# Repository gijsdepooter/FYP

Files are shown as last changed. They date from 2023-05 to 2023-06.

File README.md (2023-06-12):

# FYP
Developing a Single Channel Ultrasound Device

This project is being done with the Imperial College London Bioengineering Department, in collaboration with Prof Manos Drakakis and PhD Momen Kamal Tageldeen

This is a Repo for all the relevant material that I am developing/using for a low cost US scanner.

There are a few main parts of the US hardware:

1. The Pulser 
2. The MUX
3. The VGA (voltage gain amplifier)
4. The ADC

**PULSER**

The pulser is responsible for sending high voltage pulses to the piezo transducers in the US probe. I am using the HV7361 from microchip. It takes simple 3 bit digital instructions. These controlls are sent from the raspberry pi pico using the PIO interface to achieve precise timings.

**VGA**

The VGA controlls the amplification of the US signal and corrects for an attenuation of approximately 1dB/MHz/cm in tissue. The TGC profile is set by the MCP4921 DAC, controlled over SPI.
This is a 12 bit DAC that is controlled using the PIO interface of the rapsberry pi pico to achieve the desired speed.

**ADC** 

This project uses the LTC2236, a 10 bit DAC that can sample up to 65Msps. The ADC has a parallel output. The raspberry pi zero is used to decode the parallel ouptut using DMA and the secondary memory interface (SMI). Most of the code that controlls the ADC is from https://github.com/jbentham/rpi, and merely adapted to suit the needs of the IC of choice.

**MUX**

The multiplexer unit is an optional IC to leverage the single channel architecture of this board to controll multiple transducer channels. This allows for constructing B-Mode images with linear and phased arrays.

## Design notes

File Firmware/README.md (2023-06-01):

This contains all the firmware that operate the ultrasound board

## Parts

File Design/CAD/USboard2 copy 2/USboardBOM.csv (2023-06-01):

Source: | /Users/gijsdepooter/Desktop/UROP/CAD/USboard2 copy 2/USboard1.kicad_sch
Date: | Wednesday, 22 March 2023 at 10:44:08
Tool: | Eeschema (7.0.0-0)
Generator: | /Applications/KiCad/KiCad.app/Contents/SharedSupport/plugins/bom_csv_grouped_by_value_with_fp.py
Component Count: | 113
Ref | Qnty | Value | Cmp name | Footprint | Description | SUPPLIER | Supplier Part Number | Manufacturer | Manufacturer Part Number | Link | https://www.mouser.co.uk/ProductDetail/KYOCERA-AVX/0603ZD106KAT2A?qs=c1aAEamvUYHQhwHZOF6y0Q%3D%3D
C1 | 1 | 10uF | C | Capacitor_SMD:C_0603_1608Metric | Unpolarized capacitor | Mouser | 581-0603ZD106KAT2A | KYOCERA AVX | 0603ZD106KAT2A |  | https://www.mouser.co.uk/ProductDetail/TAIYO-YUDEN/HMJ212DC7105KGHTE?qs=DPoM0jnrROVb%2F1HhwpJMeA%3D%3D
C22, C23 | 2 | 1uF 100VDC | C | Capacitor_SMD:C_0805_2012Metric | Unpolarized capacitor | Mouser | 963-MJ212DC7105KGHTE | TAIYO YUDEN | HMJ212DC7105KGHTE |  | https://www.mouser.co.uk/ProductDetail/TDK/C0603X5R1A103K030BA
C3 | 1 | 0.01uF | C | Capacitor_SMD:C_0603_1608Metric | Unpolarized capacitor | Mouser | 581-06035C103KAT4A | KYOCERA AVX | 06035C103KAT4A |  | https://www.mouser.co.uk/ProductDetail/KEMET/C0603C104K8RAC
C59 | 1 | 22pF | C | Capacitor_SMD:C_0603_1608Metric | Unpolarized capacitor | Mouser | 603-CC603FRNPO9BN220 | YAGEO | CC0603FRNPO9BN220
C4, C5, C6, C7, C8, C9, C10, C11, C13,C18, C19, C20, C21, C24, C43, C44, C45, C46, C47, C49, C53, C55, C57, C58, C61, C63 | 28 | 0.1uF 10VDC 10% | C | Capacitor_SMD:C_0603_1608Metric | Unpolarized capacitor | Mouser | 80-C0603C104K8RAC | KEMET | C0603C104K8RAC |  | https://www.mouser.co.uk/ProductDetail/KEMET/C0603C475K8PACTU
C12 | 1 | 4.7uF | C | Capacitor_SMD:C_0603_1608Metric | Unpolarized capacitor | Mouser | 791-0603X475K100CT | WALSIN | 0603X475K100CT |  | https://www.mouser.co.uk/ProductDetail/KEMET/C0603C225K8RAC7411
C14 | 1 | 2.2uF | C | Capacitor_SMD:C_0603_1608Metric | Unpolarized capacitor | Mouser | 80-C0603C225K8R7411 | KEMET | C0603C225K8RAC7411 |  | https://www.mouser.co.uk/ProductDetail/TDK/C1608X7R1A105K080AC?qs=NRhsANhppD%252BTxQoqW7Ms9Q%3D%3D
C2, C15, C16 | 3 | 1uF 10VDC 10% | C | Capacitor_SMD:C_0603_1608Metric | Unpolarized capacitor | Mouser | 810-C1608X7R1A105K | TDK | C1608X7R1A105K080AC |  | https://www.mouser.co.uk/ProductDetail/KEMET/C0603C560J8HACTU?qs=W0yvOO0ixfEdkeZ4v%2FOkOw%3D%3D
C17 | 1 | 56pF | C | Capacitor_SMD:C_0603_1608Metric | Unpolarized capacitor | Mouser | 80-C0603C560J8HACTU | KEMET | C0603C560J8HACTU |  | https://www.mouser.co.uk/ProductDetail/KEMET/C0603C102K8RACAUTO
C50, C52, C54, C56, C62 | 5 | 1nF | C | Capacitor_SMD:C_0603_1608Metric | Unpolarized capacitor | Mouser | 80-C0603C102K8RAUTO | KEMET | C0603C102K8RACAUTO |  | https://www.mouser.co.uk/ProductDetail/TAIYO-YUDEN/HMJ107BB7104KAHT
C48, C51 | 2 | 100nF 100VDC | C | Capacitor_SMD:C_0603_1608Metric | Unpolarized capacitor | Mouser | 963-HMJ107BB7104KAHT | TAIYO YUDEN | HMJ107BB7104KAHT |  | https://www.mouser.co.uk/ProductDetail/TAIYO-YUDEN/LMK107SD183JA-T?qs=PzICbMaShUflHcZ%2F40mWUQ%3D%3D
C60 | 1 | 18nF | C | Capacitor_SMD:C_0603_1608Metric | Unpolarized capacitor | Mouser | 80-C0603C183K4R | KEMET | C0603C183K4RACTU |  | https://uk.farnell.com/diodes-inc/bav99/diode-ss-dual-100v-0-3a-sot23/dp/1902422?CMP=KNC-GUK-GEN-SKU-MDC-Test787
D1, D2, D3 | 3 | BAV99 | BAV99 | Package_TO_SOT_SMD:SOT-23 | BAV99 High-speed switching diodes, SOT-23 | Farnell | 1902422 | DIODES INC | BAV99 |  | https://www.digikey.co.uk/en/products/detail/phoenix-contact/1751264/2511021
J1 | 1 | Screw_Terminal_01x04 | Screw_Terminal_01x04 | screwConn3:1751264 | TERM BLK 4POS SIDE ENT 3.5MM PCB | Digikey | 277-5744-ND | Pheonix Contact | 1751264 |  | https://www.mouser.co.uk/ProductDetail/Adafruit/2222?qs=GURawfaeGuDZD0rNtWpsaQ%3D%3D
J2 | 1 | Raspberry_Pi_2_3 | Raspberry_Pi_2_3 | Connector_PinSocket_2.54mm:PinSocket_2x20_P2.54mm_Vertical | expansion header for Raspberry Pi 2 & 3 | Mouser | 485-2222 | Adafruit | 2222 |  | https://uk.rs-online.com/web/p/coaxial-connectors/5265785?matchtype=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
J3, J5 | 2 | Conn_Coaxial | Conn_Coaxial | Connector_Coaxial:SMA_Amphenol_132289_EdgeMount | coaxial connector SMA | RS | 526-5785 |  | 526-5785 |  | https://www.mouser.co.uk/ProductDetail/Amphenol-FCI/10129381-912003BLF?qs=0lQeLiL1qyb2GJZ3J3Epuw%3D%3D
J4 | 1 | Conn_01x12_Pin | Conn_01x12_Pin | Connector_PinHeader_2.54mm:PinHeader_2x06_P2.54mm_Vertical | Generic connector, single row, 02x6 | Mouser | 649-1012938191203BLF | Amphenol FCI | 10129381-912003BLF |  | https://www.mouser.co.uk/ProductDetail/Harwin/M22-2510205?qs=vF78I%252BjhbY%2FHssMovH2Mxg%3D%3D&mgh=1&vip=1
JP1, JP3, JP4, JP5, JP9 | 5 | Jumper_2_Open | Jumper_2_Open | Connector_PinHeader_2.00mm:PinHeader_2x01_P2.00mm_Vertical | Headers & Wire Housings 2 PIN SIL VERTICAL GOLD PIN HEADER | Mouser | 855-M22-2510205 | Harwin | M22-2510205 |  | https://www.mouser.co.uk/ProductDetail/Harwin/M22-2510205?qs=vF78I%252BjhbY%2FHssMovH2Mxg%3D%3D&mgh=1&vip=1
JP2, JP6 | 2 | Jumper_2_Bridged | Jumper_2_Bridged | Connector_PinHeader_2.00mm:PinHeader_2x01_P2.00mm_Vertical | Headers & Wire Housings 2 PIN SIL VERTICAL GOLD PIN HEADER | Mouser | 855-M22-2510205 | Harwin | M22-2510205 |  | https://www.mouser.co.uk/ProductDetail/TE-Connectivity/2355182-3?qs=Cb2nCFKsA8qFdalzWsoTCg%3D%3D&mgh=1&vip=1
L2 | 1 | Ferrite | L | Inductor_SMD:L_0603_1608Metric | Ferrite bead | Farnell | BLM18B | Murata Electronics | BLM18BB470SN1D
JP7, JP8, JP10 | 3 | Jumper_3_Bridged12 | Jumper_3_Bridged12 | Connector_PinHeader_2.00mm:PinHeader_1x03_P2.00mm_Vertical | Jumper, 3-pole, pins 1+2 closed/bridged | Mouser | 571-2355182-3 | TE Connectivity | 2355182-3 |  | https://www.mouser.co.uk/ProductDetail/Murata-Electronics/BLM18BA750SN1D?qs=eF9MexBACzorpPRQANQXVw%3D%3D
L1, L6, L7, L8, L9 | 5 | 100nH | L | Inductor_SMD:L_0603_1608Metric | Inductor | Mouser | 81-BLM18BA750SN1D | Murata Electronics | BLM18BA750SN1D |  | https://www.mouser.co.uk/ProductDetail/YAGEO/RC0603FR-07100KL?qs=e1ok2LiJcmaihem8Va5%2Fsw%3D%3D
R1 | 1 | 100K | R | Resistor_SMD:R_0603_1608Metric | Resistor | Mouser | 603-RC0603FR-07100KL | YAGEO | RC0603FR-07100KL |  | https://www.mouser.co.uk/ProductDetail/YAGEO/RT0603DRE07105KL
R2 | 1 | 105K | R | Resistor_SMD:R_0603_1608Metric | Resistor | Mouser | 603-RT0603DRE07105KL | YAGEO | RT0603DRE07105KL |  | https://www.mouser.co.uk/ProductDetail/YAGEO/RP0603BRD071KL?qs=Y0Uzf4wQF3kpBssB5AIvYA%3D%3D
R3, R4, R5, R6, R7 | 5 | 1K | R | Resistor_SMD:R_0603_1608Metric | Resistor | Mouser | 603-RP0603BRD071KL | YAGEO | RP0603BRD071KL |  | https://www.mouser.co.uk/ProductDetail/EPCOS-TDK/B82496C3101J
R8 | 1 | 49.9 | R | Resistor_SMD:R_0603_1608Metric | Resistor | Mouser | 667-ERJ-PA3F49R9V | Panasonic | ERJ-PA3F49R9V |  | https://www.mouser.co.uk/ProductDetail/YAGEO/RC0603FR-0718RL?qs=VU8sRB4EgwB41f75pR1ITg%3D%3D
R9, R10 | 2 | 18 | R | Resistor_SMD:R_0603_1608Metric | Resistor | Mouser | 603-RC0603FR-0718RL | YAGEO | RC0603FR-0718RL |  | https://www.mouser.co.uk/ProductDetail/YAGEO/RC0603FR-0733RL?qs=diQw95jMAeMotgif2GSHTQ%3D%3D
R11, R12, R13, R14, R15, R16, R17, R18, R19, R20, R21, R22, R23, R24, R25, R26 | 16 | 33 | R | Resistor_SMD:R_0603_1608Metric | Resistor | Mouser | 71-CRCW060333R0FKEAH | vISHAY / Dale | CRCW060333R0FKEAHP |  | https://www.mouser.co.uk/ProductDetail/Vishay-Dale/CRCW06034K70FKTA?qs=oYilhPf8E59EDJILyU4xpQ%3D%3D
R29, R30 | 2 | 4.7K | R | Resistor_SMD:R_0603_1608Metric | Resistor | Mouser | 71-CRCW0603-4.7K | Vishay / Draloric | CRCW06034K70FKTA |  | https://www.mouser.co.uk/ProductDetail/YAGEO/RC0603FR-0710KL?qs=grNVn54RoB%252B3GtjbJj3wJQ%3D%3D
R31, R41, R42, | 3 | 10K | R | Resistor_SMD:R_0603_1608Metric | Resistor | Mouser | 603-RC0603FR-0710KL | YAGEO | RC0603FR-0710KL |  | https://www.mouser.co.uk/ProductDetail/Bourns/CR0603-FX-1000ELF?qs=K5ddiUFZPT7prY7pGcr1LQ%3D%3D
R37, R38 | 2 | 100 | R | Resistor_SMD:R_0603_1608Metric | Resistor | Mouser | 652-CR0603FX-1000ELF | Bourns | CR0603-FX-1000ELF |  | https://www.mouser.co.uk/ProductDetail/YAGEO/AC0603FR-0711KL?qs=sGAEpiMZZMtlubZbdhIBINBo7nw4llFtNj40dcv4WFE%3D
R39 | 1 | 11k | R | Resistor_SMD:R_0603_1608Metric | Resistor | Mouser | 603-AC0603FR-0711KL | YAGEO | AC0603FR-0711KL |  | https://www.mouser.co.uk/ProductDetail/YAGEO/AC0603FR-07280RL
R43 | 1 | 280 | R | Resistor_SMD:R_0603_1608Metric | Resistor | Mouser | 603-AC0603FR-07280RL | YAGEO | AC0603FR-07280RL |  | https://www.mouser.co.uk/ProductDetail/Microchip-Technology-Atmel/MD0100N8-G?qs=0AMA1uIX0FIE5iDlCsAHAw%3D%3D
U2 | 1 | MD0100N8-G | MD0100N8-G | MDO100:MD0100N8-G | T/R protection switch | Mouser | 689-MD0100N8-G | Microchip | MD0100N8-G |  | https://www.mouser.co.uk/ProductDetail/Microchip-Technology/MCP4725A3T-E-CH?qs=hH%252BOa0VZEiBSYoLvaYdGYg%3D%3D
U4 | 1 | MCP4725A3T-E/CH | MCP4725A3T-E/CH | Package_TO_SOT_SMD:SOT-23-6 | 12-bit Digital-to-Analog Converter, integrated EEPROM, I2C interface, SOT-23-6 | Mouser | 579-MCP4725A3T-E/CH | Microchip | MCP4725A3T-E/CH |  | https://www.mouser.co.uk/ProductDetail/Analog-Devices/LT1763IS8-3.3PBF?qs=ytflclh7QUXoCHefIThm8A%3D%3D
U5 | 1 | LT1763IS8-3.3-PBF | LT1763IS8-3.3-PBF | VCCsup:LT1763IS8-3.3-PBF | Voltage regulator | Mouser | 584-LT1763IS8-3.3PBF | Analog Devices | LT1763IS8-3.3#PBF |  | https://dk.farnell.com/en-DK/on-semiconductor/nc7svu04p5x/inverter-gate-single-1-i-p-sc/dp/2453123
U6 | 1 | NC7SVU04P5X | NC7SVU04P5X | INVERTER:NC7SVU04P5X | Inverter | Farnell | 2453123 | ONSEMI | NC7SVU04P5X
U1 | 1 | LTC2236IUH-PBF | LTC2236:LTC2236IUH-PBF | ADC 25MSPS 10BIT |  | Mouser | 584-LTC2236IUH#PBF | Analog Devices | LTC2236IUH#PBF |  | £9.64 | https://www.mouser.co.uk/ProductDetail/Analog-Devices/LTC2236CUHPBF?qs=hVkxg5c3xu9mjIScvNp8xw%3D%3D
U3 | 1 | 74VCX16373MTD | Latch:74VCX16373MTD | LOGIC LATCH |  | Mouser | 512-74VCX16373MTD | onsemi / Fairchild | 74VCX16373MTD |  | £1.73 | https://www.mouser.co.uk/ProductDetail/onsemi-Fairchild/74VCX16373MTD?qs=bX5Pkui%252BodUH7A1197lniw%3D%3D
U7 | 1 | HV7361GA-G | HV7361:HV7361GA-G | PULSER |  | Mouser | 579-HV7361GA-G | Microchip | HV7361GA-G |  | £8.98 | https://www.mouser.co.uk/ProductDetail/579-HV7361GA-G
U11 | 1 | AD8331ARQZ | AD8331:SOP64P600X175-20N | AD8331ARQZ, Programmable Gain Amplifier, 20-Pin QSOP |  | Mouser | 584-AD8331ARQZ | Analog Devices | AD8331ARQZ |  | £12.44 | https://www.mouser.co.uk/ProductDetail/Analog-Devices/AD8331ARQZ-R7?qs=%2FtpEQrCGXCysgac2siIaMw%3D%3D

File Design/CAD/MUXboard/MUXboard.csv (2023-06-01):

Source: | /Users/gijsdepooter/Desktop/Desktop - Gijs’s MacBook Pro/UROP/MUXboard/MUXboard.kicad_sch
Date: | Monday, 24 April 2023 at 08:52:58
Tool: | Eeschema (7.0.0-0)
Generator:
Component Count: | 9
Ref | Qnty | Value | Cmp name | Description | Supplier | Supplier Part Number | Manufacturer | MPN
C1, C2 | 2 | 1u | C | Unpolarized capacitor | Mouser | 810-C1608X7R1A105K | TDK | C1608X7R1A105K080AC | https://www.mouser.co.uk/ProductDetail/TDK/C1608X7R1A105K080AC?qs=NRhsANhppD%252BTxQoqW7Ms9Q%3D%3D
IC1 | 1 | HV2607T-C_R8X | HV2607T-C_R8X | HV2607T-C/R8X | Digikey | 150-HV2607T-C/R8XTR-ND | Microchip Technology | HV2607T-C/R8X
J1, J2 | 2 | Conn_Coaxial | Conn_Coaxial_1 | coaxial connector SMA | RS | 180-9922 | Wurth Elektronik | 6.03142E+13 | https://uk.rs-online.com/web/p/coaxial-connectors/1809922
J4 | 1 | Conn_01x16_Pin | Conn_01x16_Pin | Generic connector, single row, 01x16, script generated | Mouser | 200-TSW10808LD | Samtec | TSW-108-08-L-D | https://www.mouser.co.uk/ProductDetail/Samtec/TSW-108-08-L-D?qs=rU5fayqh%252BE3wWhrtuP8e1w%3D%3D
J5 | 1 | Conn_01x12_Pin | Conn_01x12_Pin | Generic connector, single row, 01x12, script generated | Mouser | 649-1012938191203BLF | Amphenol FCI | 10129381-912003BLF | https://www.mouser.co.uk/ProductDetail/Amphenol-FCI/10129381-912003BLF?qs=0lQeLiL1qyb2GJZ3J3Epuw%3D%3D
JP1 | 1 | Jumper_2_Open | Jumper_2_Open | Jumper, 2-pole, open | Mouser | 855-M22-2510205 | Harwin | M22-2510205 | https://www.mouser.co.uk/ProductDetail/Harwin/M22-2510205?qs=vF78I%252BjhbY%2FHssMovH2Mxg%3D%3D
R1, R2, R3, R4, R5 | 5 | 10K | R | Resistor | Mouser | 603-RC0603FR-0710KL | YAGEO | RC0603FR-0710KL | https://www.mouser.co.uk/ProductDetail/YAGEO/RC0603FR-0710KL?qs=grNVn54RoB%252B3GtjbJj3wJQ%3D%3D

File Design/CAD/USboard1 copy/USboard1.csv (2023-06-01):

chip | quantity | name |  |  |  | link
U1 | 1 | LTC2236IUH-PBF | LTC2236:LTC2236IUH-PBF | ADC 25MSPS 10BIT | Mouser | https://www.mouser.co.uk/ProductDetail/Analog-Devices/LTC2236CUHPBF?qs=hVkxg5c3xu9mjIScvNp8xw%3D%3D
U2 | 1 | MD0100N8-G | MDO100:MD0100N8-G | T/R SWITCH | Mouser | https://www.mouser.co.uk/ProductDetail/Microchip-Technology-Atmel/MD0100N8-G?qs=0AMA1uIX0FIE5iDlCsAHAw%3D%3D
U3 | 1 | 74VCX16373MTD | Latch:74VCX16373MTD | LOGIC LATCH | Mouser | https://www.mouser.co.uk/ProductDetail/onsemi-Fairchild/74VCX16373MTD?qs=bX5Pkui%252BodUH7A1197lniw%3D%3D
U4 | 1 | MCP4725A3T-E/CH | Package_TO_SOT_SMD:SOT-23-6 | 12-bit Digital-to-Analog Converter, integrated EEPROM, I2C interface, SOT-23-6 | Mouser | https://www.mouser.co.uk/ProductDetail/Microchip-Technology/MCP4725A3T-E-CH?qs=hH%252BOa0VZEiBSYoLvaYdGYg%3D%3D
U10 | 1 | HV7361GA-G | HV7361:HV7361GA-G | PULSER | Mouser | https://www.mouser.co.uk/ProductDetail/579-HV7361GA-G
U11 | 1 | AD8331ARQZ | AD8331:SOP64P600X175-20N | AD8331ARQZ, Programmable Gain Amplifier, 20-Pin QSOP | Mouser | https://www.mouser.co.uk/ProductDetail/Analog-Devices/AD8331ARQZ-R7?qs=%2FtpEQrCGXCysgac2siIaMw%3D%3D

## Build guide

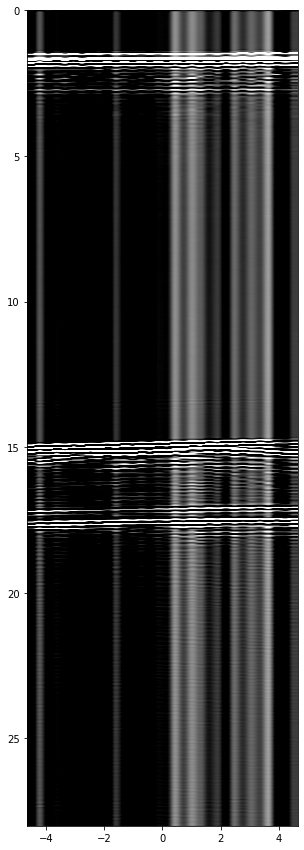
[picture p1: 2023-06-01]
Image_construction/Figure 2022-07-15 182849.png

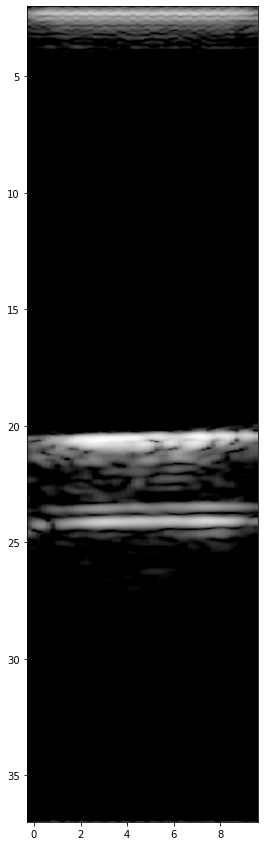
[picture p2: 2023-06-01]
Image_construction/Figure 2022-07-19 131949.png

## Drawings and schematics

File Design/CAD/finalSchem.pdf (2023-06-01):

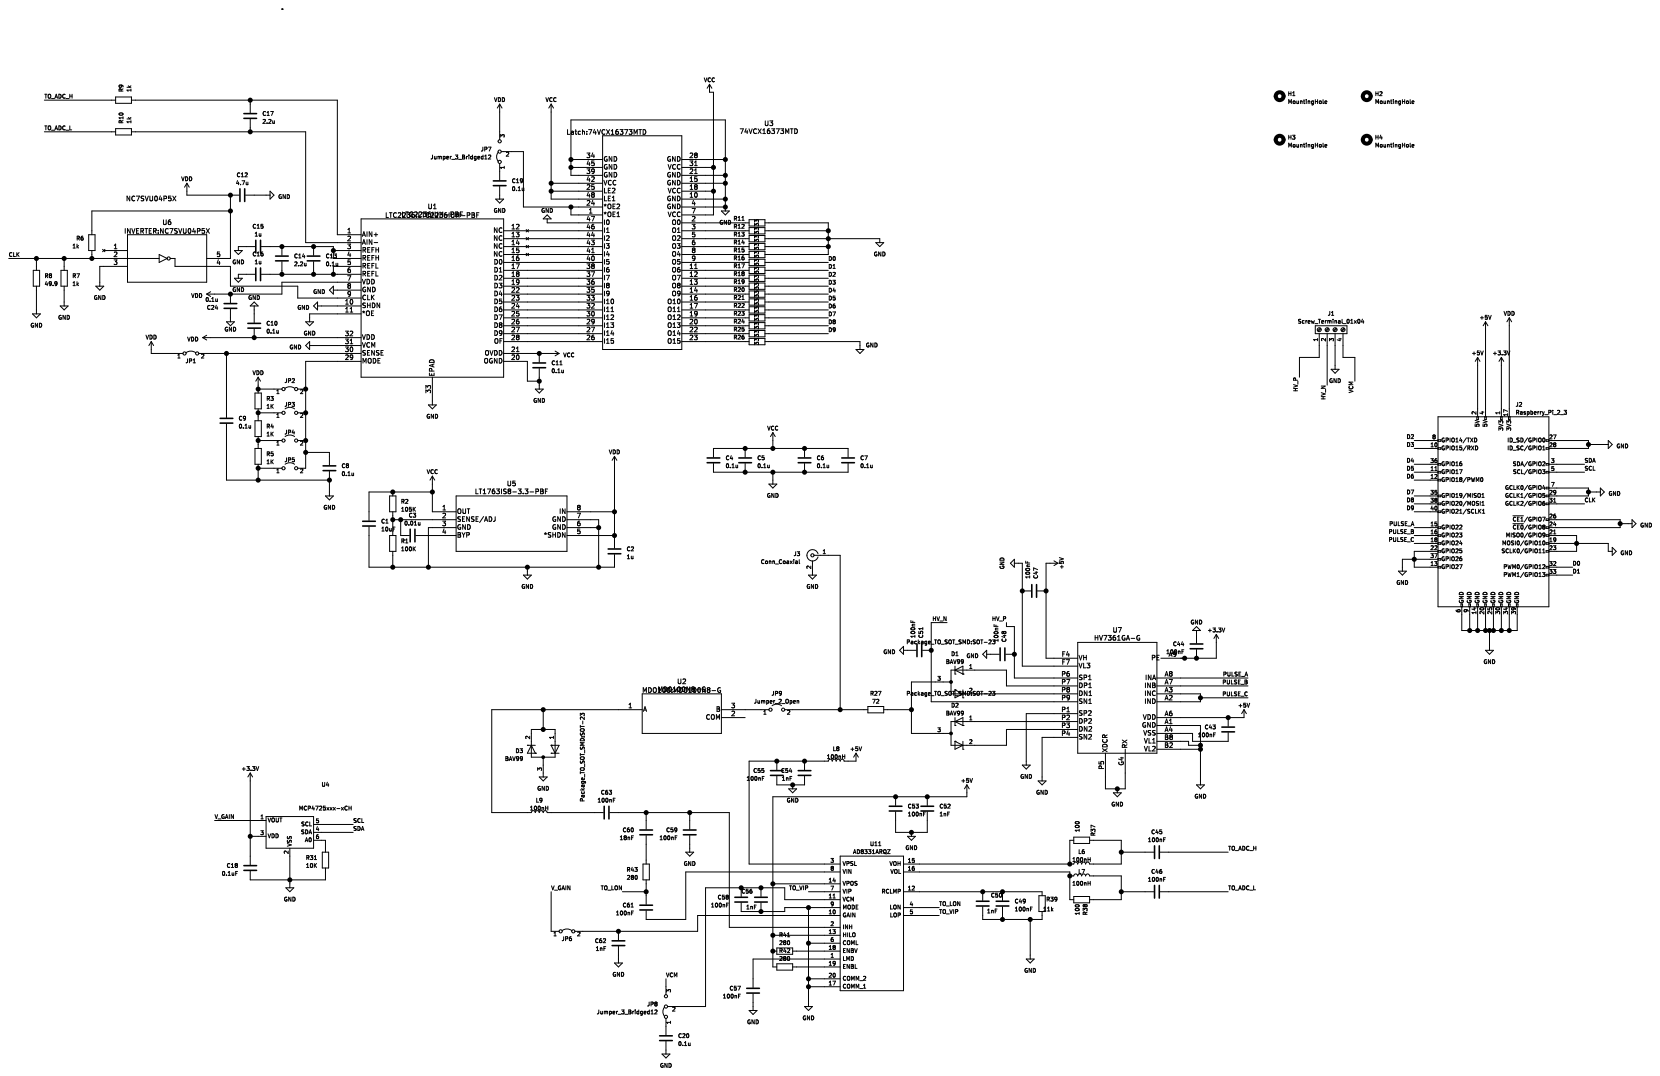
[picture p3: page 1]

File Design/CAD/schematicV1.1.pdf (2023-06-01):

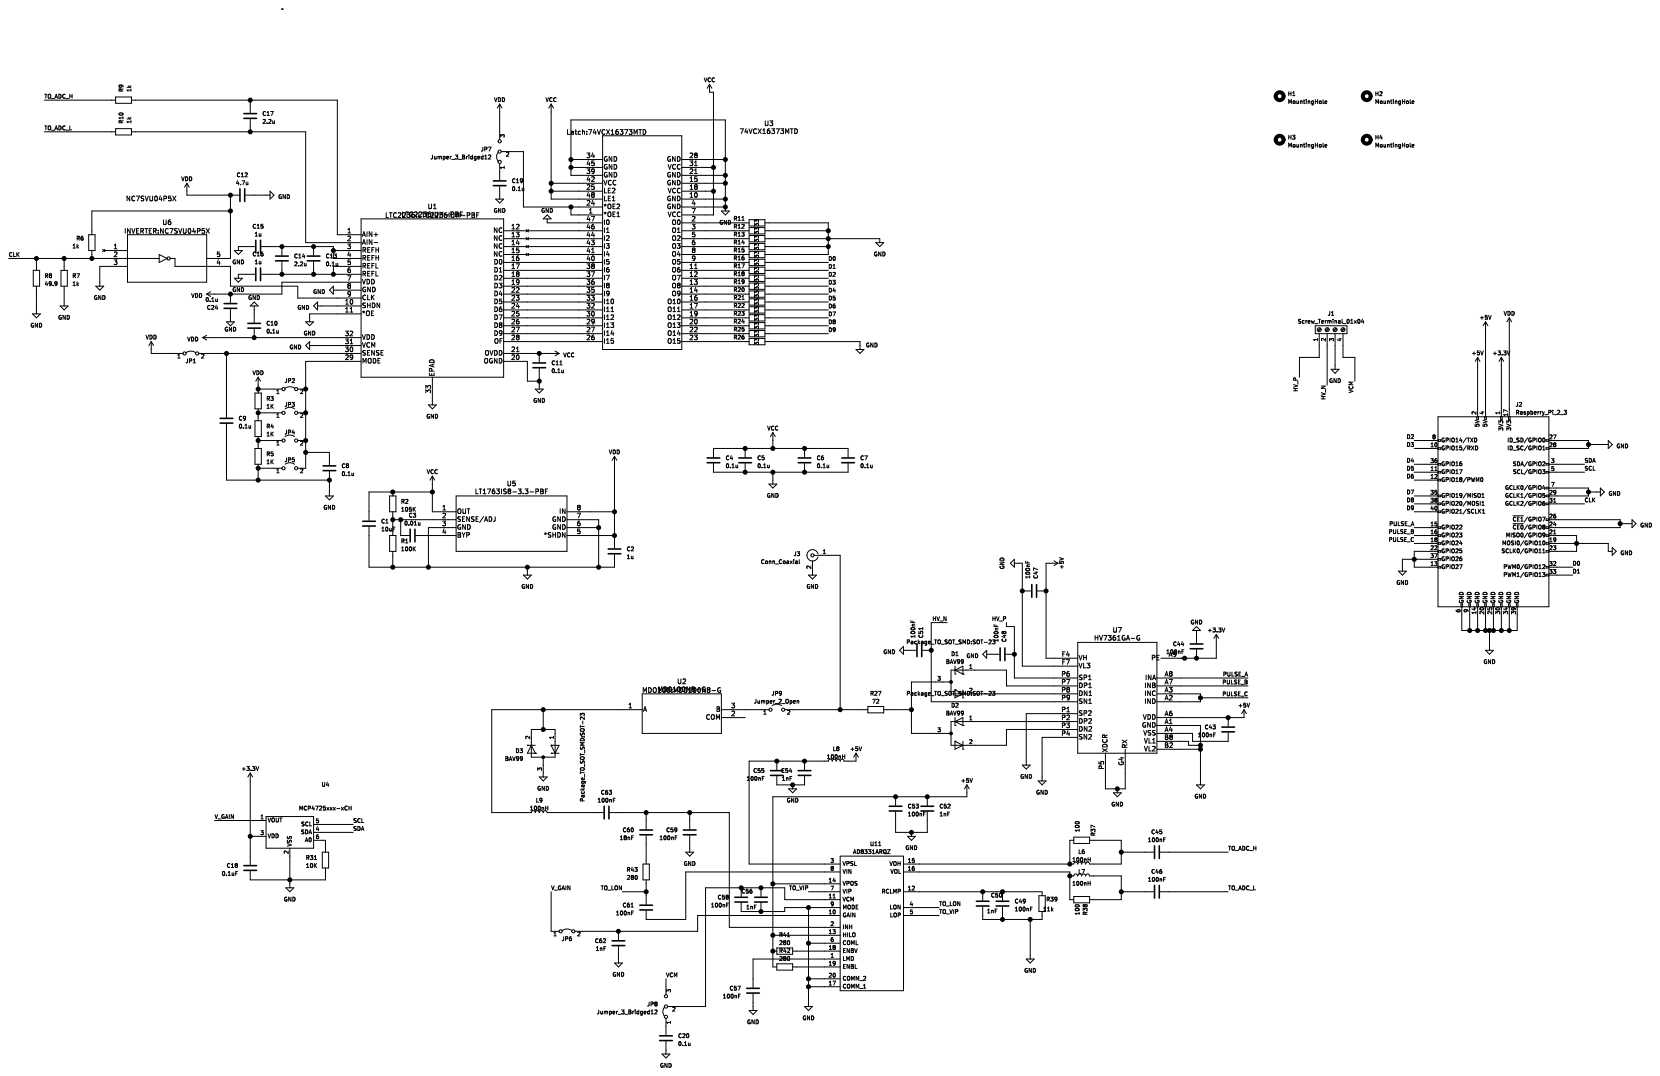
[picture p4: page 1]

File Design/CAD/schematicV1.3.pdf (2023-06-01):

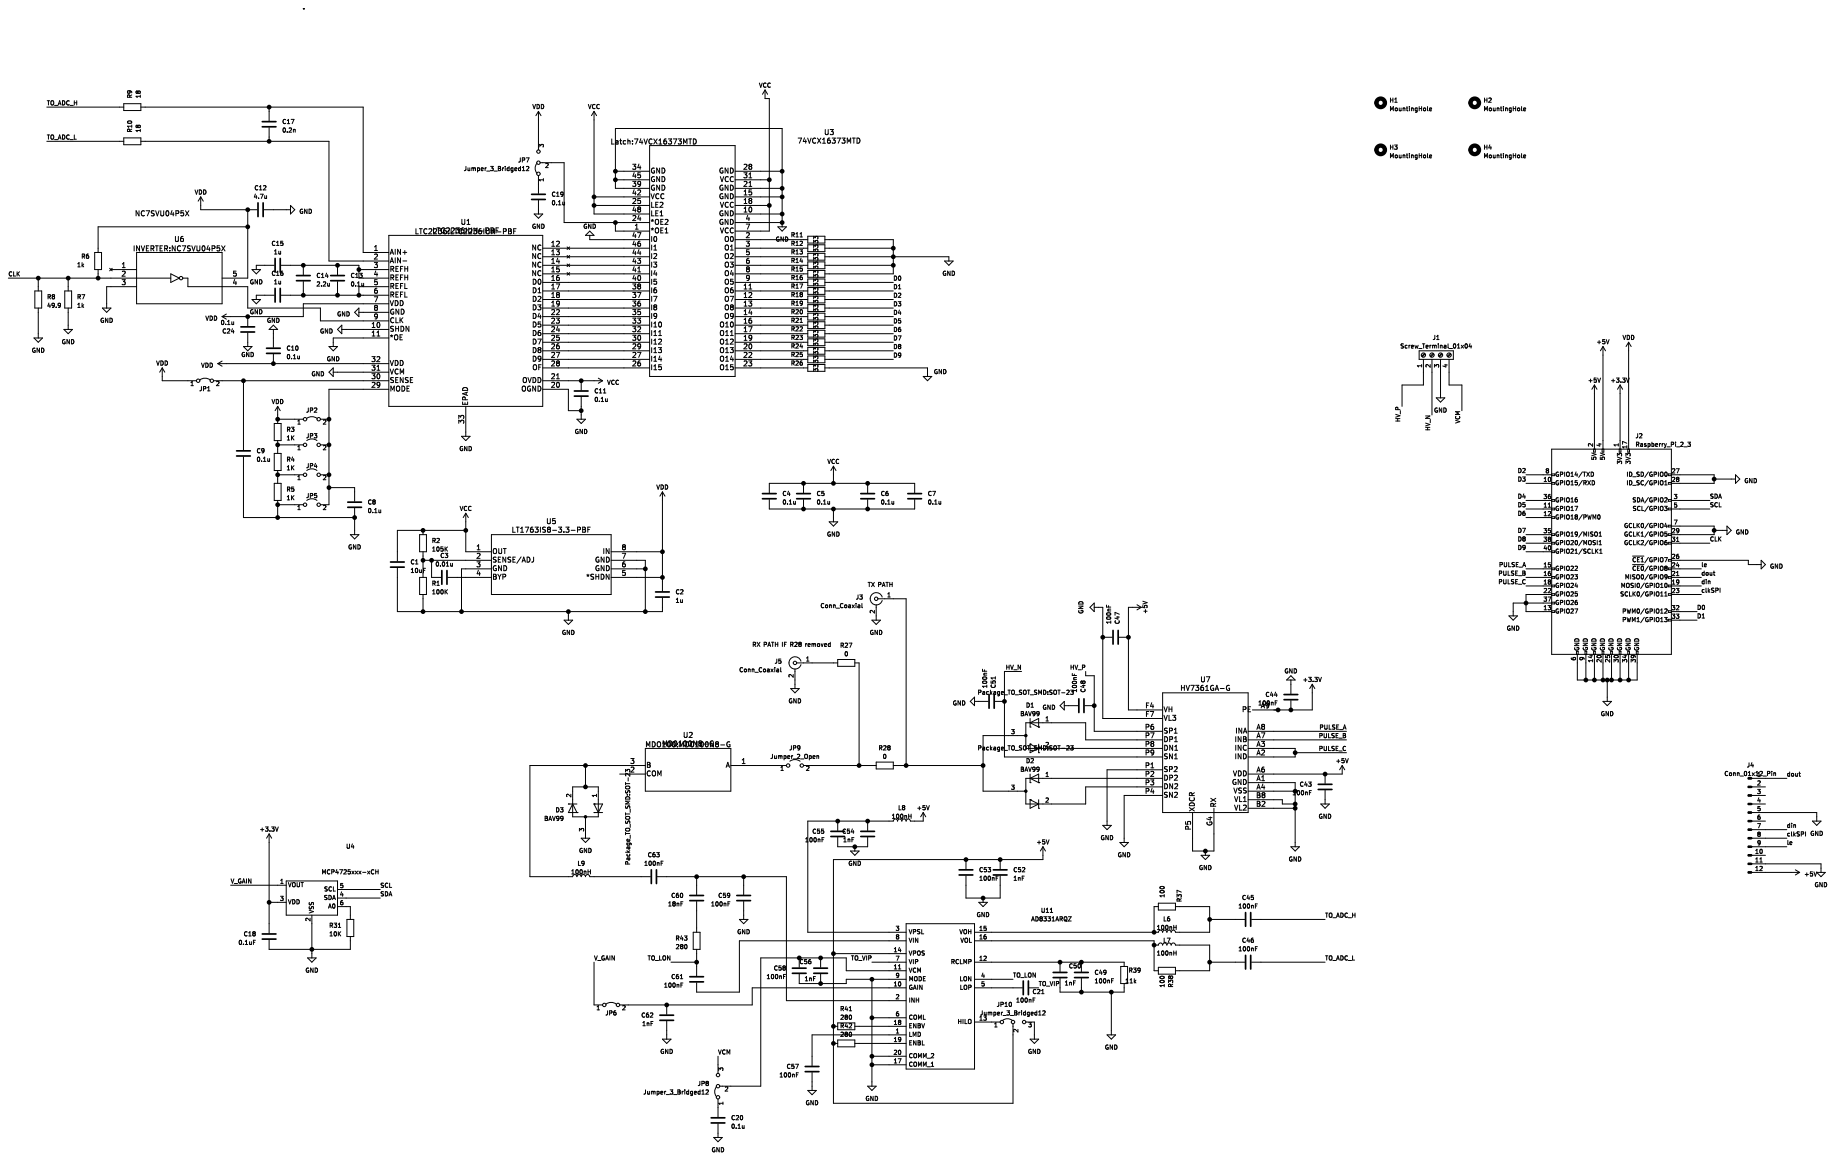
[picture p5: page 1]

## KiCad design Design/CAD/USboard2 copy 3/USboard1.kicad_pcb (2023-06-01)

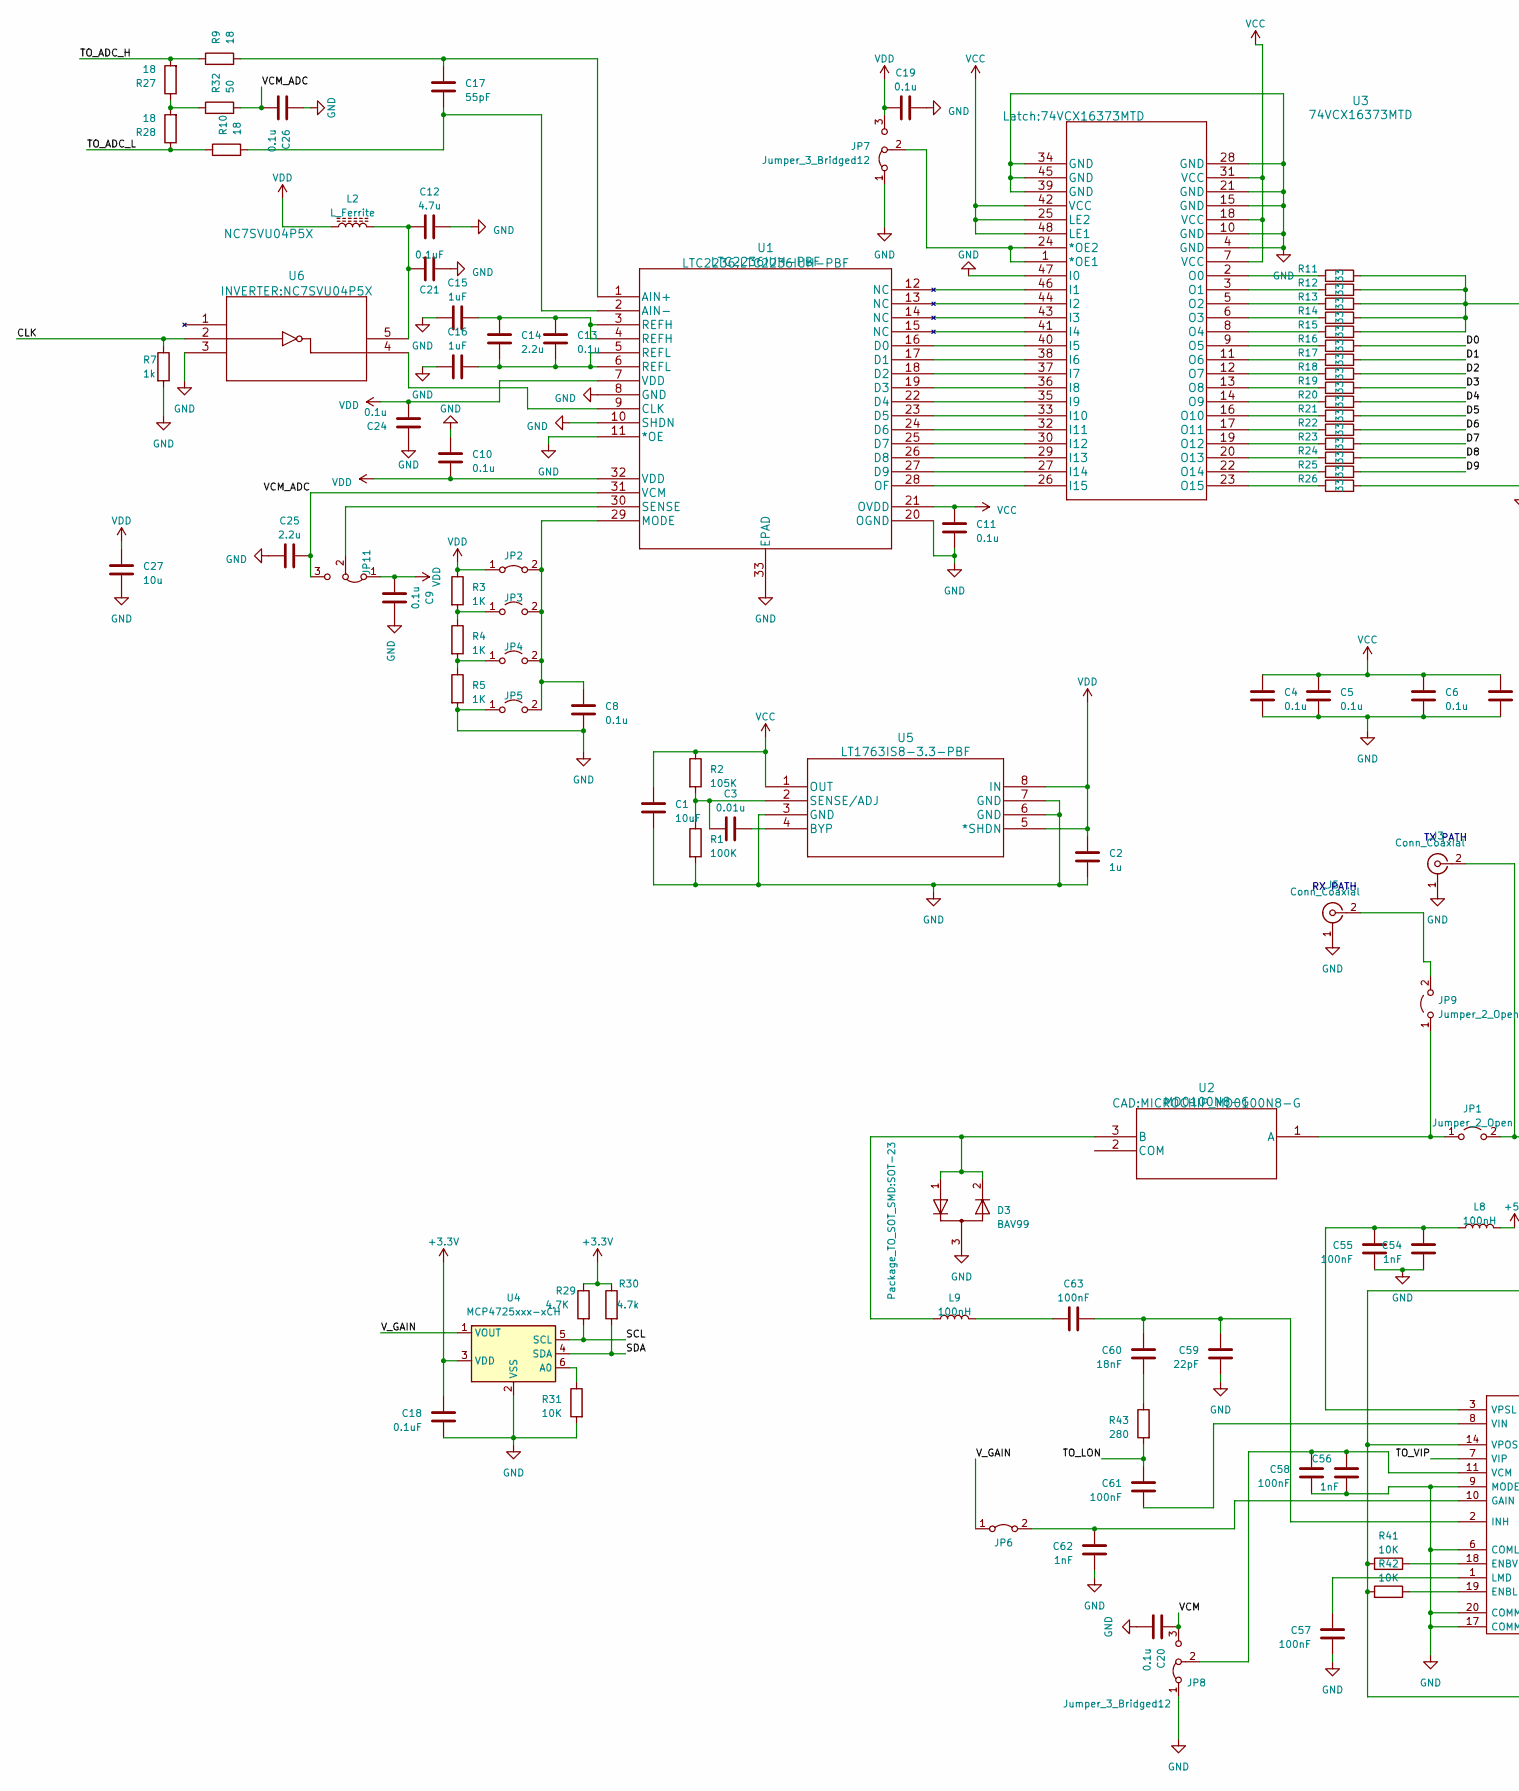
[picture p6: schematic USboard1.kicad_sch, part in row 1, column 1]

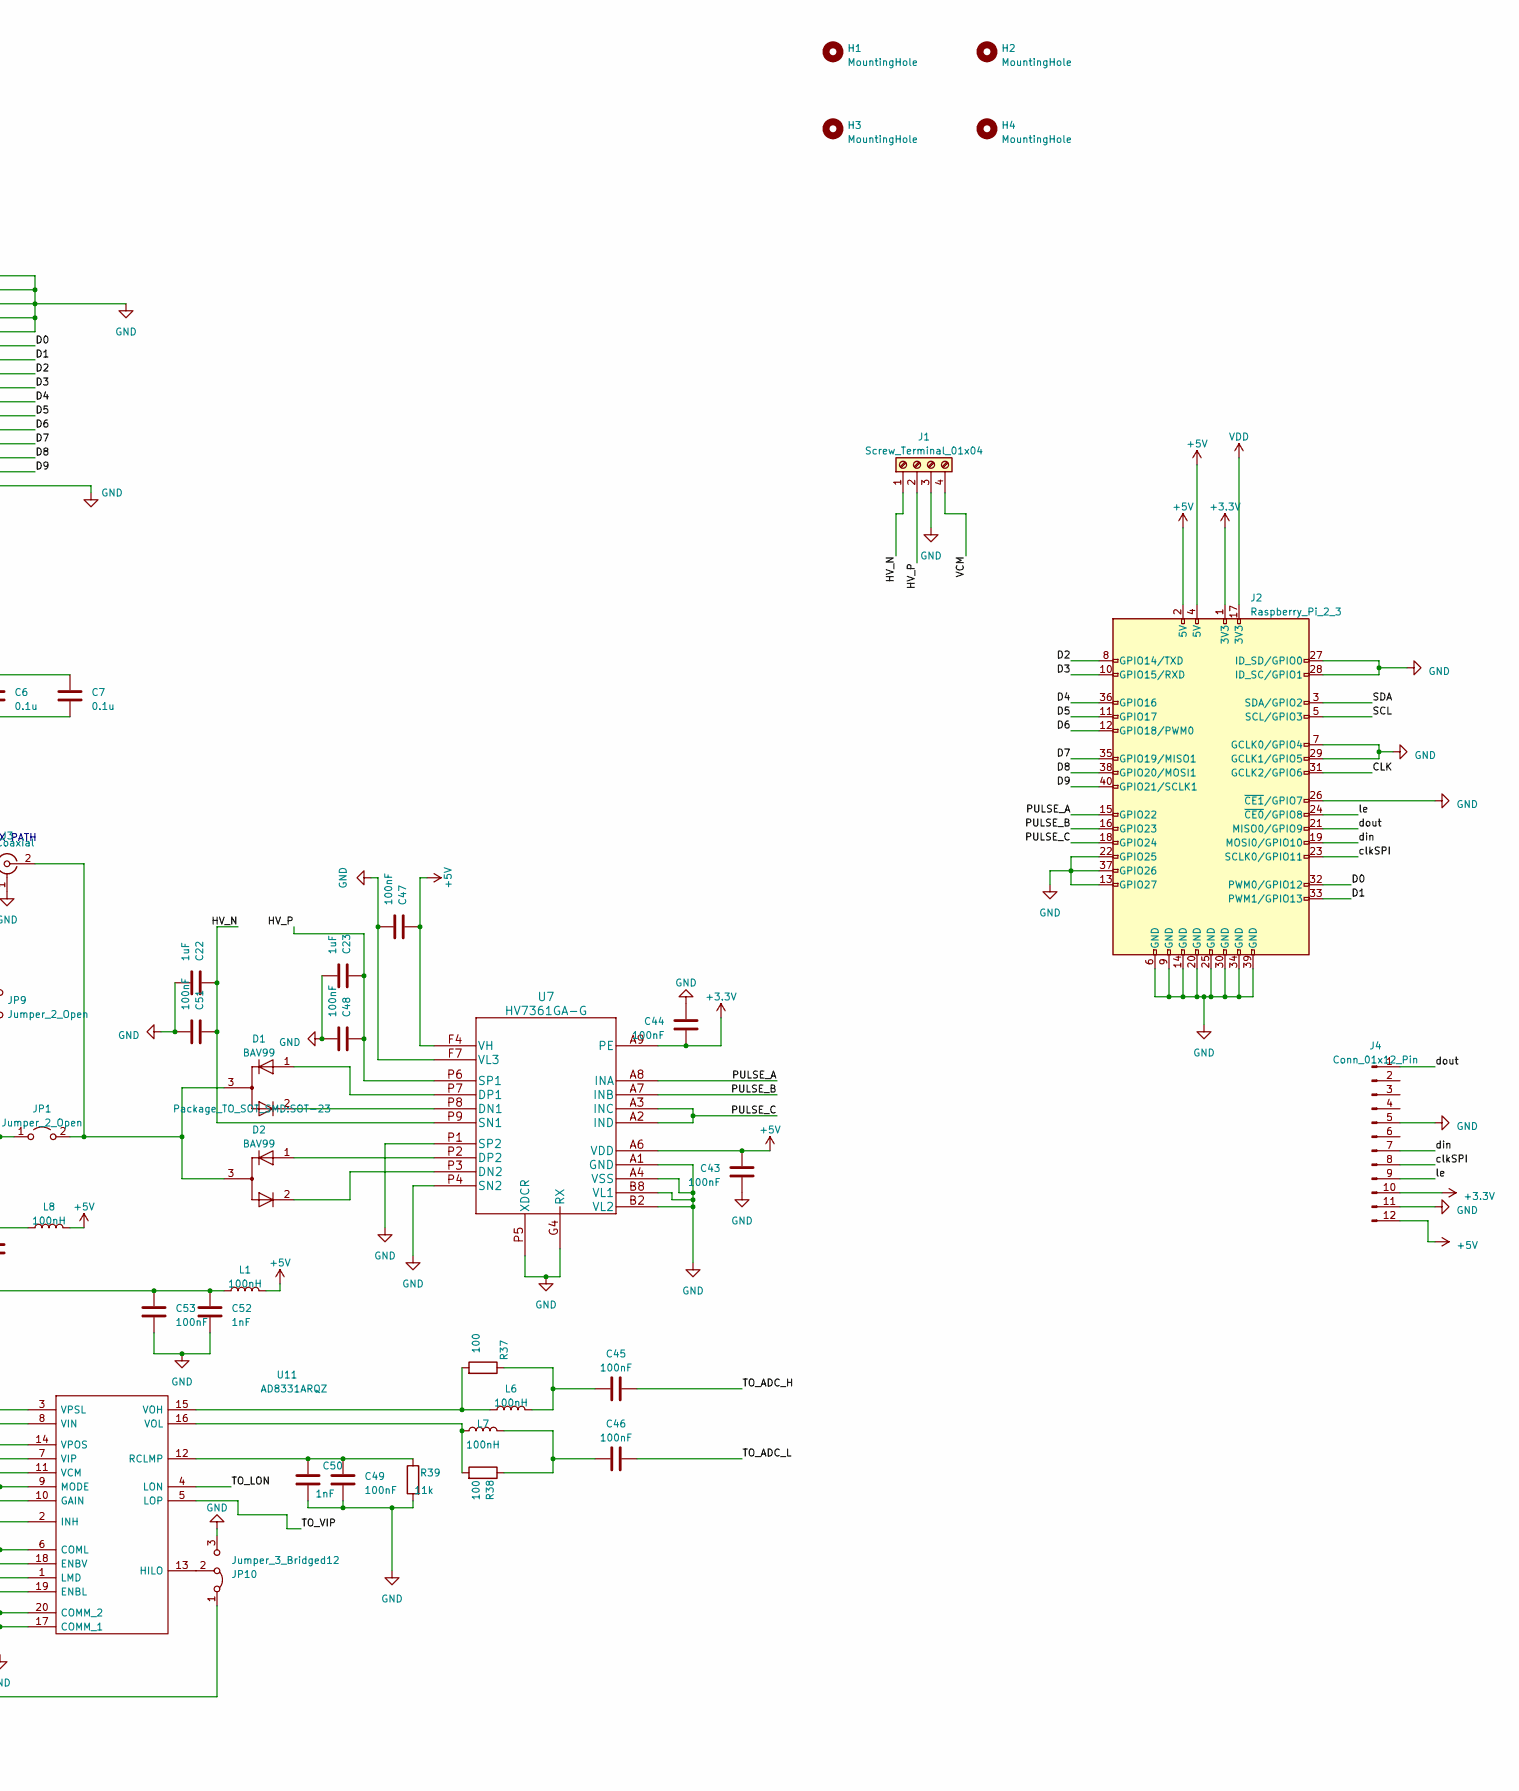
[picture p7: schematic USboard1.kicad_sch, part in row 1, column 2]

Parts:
C1: 10uF; C_0603_1608Metric
C2: 1u; C_0603_1608Metric
C3: 0.01u; C_0603_1608Metric
C4, C5, C6, C7, C8, C9, C10, C11, C13, C19, C20, C24, C26: 0.1u; C_0603_1608Metric
C12: 4.7u; C_0603_1608Metric
C14, C25: 2.2u; C_0603_1608Metric
C15, C16: 1uF; C_0603_1608Metric
C17: 55pF; C_0603_1608Metric
C18, C21: 0.1uF; C_0603_1608Metric
C22, C23: 1uF; C_0805_2012Metric
C27: 10u; C_0603_1608Metric
C43, C44, C45, C46, C47, C48, C49, C51, C53, C55, C57, C58, C61, C63: 100nF; C_0603_1608Metric
C50, C52, C54, C56, C62: 1nF; C_0603_1608Metric
C59: 22pF; C_0603_1608Metric
C60: 18nF; C_0603_1608Metric
D1, D2, D3: BAV99; SOT-23
H1, H2, H3, H4: MountingHole; MountingHole_3.5mm
J1: Screw_Terminal_01x04; 1751264
J2: Raspberry_Pi_2_3; PinSocket_2x20_P2.54mm_Vertical
J3, J5: Conn_Coaxial; RS_526-5785
J4: Conn_01x12_Pin; PinHeader_2x06_P2.54mm_Vertical
JP1, JP3, JP4, JP5, JP9: Jumper_2_Open; PinHeader_2x01_P2.00mm_Vertical
JP2, JP6: Jumper_2_Bridged; PinHeader_2x01_P2.00mm_Vertical
JP7, JP8, JP10, JP11: Jumper_3_Bridged12; PinHeader_1x03_P2.00mm_Vertical
L1, L6, L7, L8, L9: 100nH; L_0603_1608Metric
L2: L_Ferrite; L_0603_1608Metric
R1: 100K; R_0603_1608Metric
R2: 105K; R_0603_1608Metric
R3, R4, R5: 1K; R_0603_1608Metric
R7: 1k; R_0603_1608Metric
R9, R10, R27, R28: 18; R_0603_1608Metric
R11, R12, R13, R14, R15, R16, R17, R18, R19, R20, R21, R22, R23, R24, R25, R26: 33; R_0603_1608Metric
R29: 4.7K; R_0603_1608Metric
R30: 4.7k; R_0603_1608Metric
R31, R41, R42: 10K; R_0603_1608Metric
R32: 50; R_0603_1608Metric
R37, R38: 100; R_0603_1608Metric
R39: 11k; R_0603_1608Metric
R43: 280; R_0603_1608Metric
U1: LTC2236IUH-PBF
U2: MD0100N8-G; MICROCHIP_MD0100N8-G
U3: 74VCX16373MTD
U4: MCP4725xxx-xCH; SOT-23-6
U5: LT1763IS8-3.3-PBF
U6: NC7SVU04P5X
U7: HV7361GA-G
U11: AD8331ARQZ; SOP64P600X175-20N; Manufacturer_Part_Number AD8331ARQZ; Mouser Part Number 584-AD8331ARQZ

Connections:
+3.3V: C18.1, C44.2, J2.1 (3V3), J4.10, R29.1, R30.1, U4.3 (VDD), U7.A9 (PE)
+5V: C43.1, C47.1, J2.2 (5V), J2.4 (5V), J4.12, L1.1, L8.1, U7.A6 (VDD), U7.F4 (VH)
/CLK: J2.31 (GCLK2/GPIO6), R7.1, U6.2 (A)
/D0: J2.32 (PWM0/GPIO12), R16.2
/D1: J2.33 (PWM1/GPIO13), R17.2
/D2: J2.8 (GPIO14/TXD), R18.2
/D3: J2.10 (GPIO15/RXD), R19.2
/D4: J2.36 (GPIO16), R20.2
/D5: J2.11 (GPIO17), R21.2
/D6: J2.12 (GPIO18/PWM0), R22.2
/D7: J2.35 (GPIO19/MISO1), R23.2
/D8: J2.38 (GPIO20/MOSI1), R24.2
/D9: J2.40 (GPIO21/SCLK1), R25.2
/HV_N: C22.1, C51.1, J1.1, U7.P9 (SN1)
/HV_P: C23.1, C48.1, J1.2, U7.P6 (SP1)
/PULSE_A: J2.15 (GPIO22), U7.A8 (INA)
/PULSE_B: J2.16 (GPIO23), U7.A7 (INB)
/PULSE_C: J2.18 (GPIO24), U7.A2 (IND), U7.A3 (INC)
/SCL: J2.5 (SCL/GPIO3), R29.2, U4.5 (SCL)
/SDA: J2.3 (SDA/GPIO2), R30.2, U4.4 (SDA)
/TO_ADC_H: C45.1, R9.1, R27.2
/TO_ADC_L: C46.1, R10.1, R28.1
/TO_LON: C61.1, R43.2, U11.4 (LON)
/TO_VIP: U11.5 (LOP), U11.7 (VIP)
/VCM: C20.1, J1.4, JP8.3 (B)
/VCM_ADC: C25.2, C26.2, JP11.3 (B), R32.2, U1.31 (VCM)
/V_GAIN: JP6.1 (A), U4.1 (VOUT)
/clkSPI: J2.23 (SCLK0/GPIO11), J4.8
/din: J2.19 (MOSI0/GPIO10), J4.7
/dout: J2.21 (MISO0/GPIO9), J4.1
/le: J2.24 (~CE0/GPIO8), J4.9
GND: C1.2, C2.2, C4.2, C5.2, C6.2, C7.2, C8.2, C9.2, C10.1, C11.2, C12.2, C15.2, C16.2, C18.2, C19.2, C20.2, C21.2, C22.2, C23.2, C24.1, C25.1, C26.1, C27.1, C43.2, C44.1, C47.2, C48.2, C49.2, C50.2, C51.2, C52.2, C53.2, C54.2, C55.2, C56.2, C57.2, C58.2, C59.2, C62.2, D3.3 (K), J1.3, J2.6 (GND), J2.7 (GCLK0/GPIO4), J2.9 (GND), J2.13 (GPIO27), J2.14 (GND), J2.20 (GND), J2.22 (GPIO25), J2.25 (GND), J2.26 (~CE1/GPIO7), J2.27 (ID_SD/GPIO0), J2.28 (ID_SC/GPIO1), J2.29 (GCLK1/GPIO5), J2.30 (GND), J2.34 (GND), J2.37 (GPIO26), J2.39 (GND), J3.1 (In), J4.5, J4.11, J5.1 (In), JP5.1 (A), JP7.1 (A), JP8.1 (A), JP10.3 (B), R1.2, R5.2, R7.2, R11.2, R12.2, R13.2, R14.2, R15.2, R26.2, R31.2, R39.2, U1.8 (GND), U1.10 (SHDN), U1.11 (*OE), U1.20 (OGND), U1.33 (EPAD), U3.4 (GND), U3.10 (GND), U3.15 (GND), U3.21 (GND), U3.28 (GND), U3.34 (GND), U3.39 (GND), U3.45 (GND), U3.47 (I0), U4.2 (VSS), U5.3 (GND), U5.6 (GND), U5.7 (GND), U6.3 (GND), U7.A1 (GND), U7.A4 (VSS), U7.B2 (VL2), U7.B8 (VL1), U7.F7 (VL3), U7.G4 (RX), U7.P1 (SP2), U7.P4 (SN2), U7.P5 (XDCR), U11.6 (COML), U11.9 (MODE), U11.17 (COMM_1), U11.20 (COMM_2)
unnamed: C13.1, C14.1, C15.1, U1.3 (REFH), U1.4 (REFH)
unnamed: C13.2, C14.2, C16.1, U1.5 (REFL), U1.6 (REFL)
unnamed: C45.2, L6.1, R37.1
unnamed: C46.2, L7.1, R38.1
unnamed: C60.2, R43.1
unnamed: C63.1, L9.1
unnamed: D1.2 (A), U7.P8 (DN1)
unnamed: D2.2 (A), U7.P3 (DN2)
unnamed: D3.1 (K), D3.2 (A), L9.2, U2.3 (B)
unnamed: D1.3 (K), D2.3 (K), J3.2 (Ext), JP1.2 (B)
unnamed: J5.2 (Ext), JP9.2 (B)
unnamed: JP1.1 (A), JP9.1 (A), U2.1 (A)
unnamed: C8.1, JP2.2 (B), JP3.2 (B), JP4.2 (B), JP5.2 (B), U1.29 (MODE)
unnamed: JP3.1 (A), R3.2, R4.1
unnamed: JP4.1 (A), R4.2, R5.1
unnamed: C62.1, JP6.2 (B), U11.10 (GAIN)
unnamed: JP7.2 (C), U3.1 (*OE1), U3.24 (*OE2)
unnamed: C56.1, C58.1, JP8.2 (C), U11.11 (VCM)
unnamed: C52.1, C53.1, JP10.1 (A), L1.2, R41.2, R42.2, U11.14 (VPOS)
unnamed: JP10.2 (C), U11.13 (HILO)
unnamed: JP11.2 (C), U1.30 (SENSE)
unnamed: R27.1, R28.2, R32.1
unnamed: C17.1, R9.2, U1.1 (AIN+)
unnamed: C17.2, R10.2, U1.2 (AIN-)
unnamed: U1.9 (CLK), U6.4 (Y)
unnamed: U1.16 (D0), U3.40 (I5)
unnamed: U1.17 (D1), U3.38 (I6)
unnamed: U1.18 (D2), U3.37 (I7)
unnamed: U1.19 (D3), U3.36 (I8)
unnamed: U1.22 (D4), U3.35 (I9)
unnamed: U1.23 (D5), U3.33 (I10)
unnamed: U1.24 (D6), U3.32 (I11)
unnamed: U1.25 (D7), U3.30 (I12)
unnamed: U1.26 (D8), U3.29 (I13)
unnamed: U1.27 (D9), U3.27 (I14)
unnamed: U1.28 (OF), U3.26 (I15)
unnamed: R11.1, U3.2 (O0)
unnamed: R12.1, U3.3 (O1)
unnamed: R13.1, U3.5 (O2)
unnamed: R14.1, U3.6 (O3)
unnamed: R15.1, U3.8 (O4)
unnamed: R16.1, U3.9 (O5)
unnamed: R17.1, U3.11 (O6)
unnamed: R18.1, U3.12 (O7)
unnamed: R19.1, U3.13 (O8)
unnamed: R20.1, U3.14 (O9)
unnamed: R21.1, U3.16 (O10)
unnamed: R22.1, U3.17 (O11)
unnamed: R23.1, U3.19 (O12)
unnamed: R24.1, U3.20 (O13)
unnamed: R25.1, U3.22 (O14)
unnamed: R26.1, U3.23 (O15)
unnamed: R31.1, U4.6 (A0)
unnamed: C3.2, U5.4 (BYP)
unnamed: C3.1, R1.1, R2.2, U5.2 (SENSE/ADJ)
unnamed: C12.1, C21.1, L2.2, U6.5 (VCC)
unnamed: D1.1 (K), U7.P7 (DP1)
unnamed: D2.1 (K), U7.P2 (DP2)
unnamed: R42.1, U11.19 (ENBL)
unnamed: R41.1, U11.18 (ENBV)
unnamed: C59.1, C60.1, C63.2, U11.2 (INH)
unnamed: C57.1, U11.1 (LMD)
unnamed: C49.1, C50.1, R39.1, U11.12 (RCLMP)
unnamed: C61.2, U11.8 (VIN)
unnamed: L6.2, R37.2, U11.15 (VOH)
unnamed: L7.2, R38.2, U11.16 (VOL)
unnamed: C54.1, C55.1, L8.2, U11.3 (VPSL)
VCC: C1.1, C4.1, C5.1, C6.1, C7.1, C11.1, R2.1, U1.21 (OVDD), U3.7 (VCC), U3.18 (VCC), U3.25 (LE2), U3.31 (VCC), U3.42 (VCC), U3.48 (LE1), U5.1 (OUT)
VDD: C2.1, C9.1, C10.2, C19.1, C24.2, C27.2, J2.17 (3V3), JP2.1 (A), JP7.3 (B), JP11.1 (A), L2.1, R3.1, U1.7 (VDD), U1.32 (VDD), U5.5 (*SHDN), U5.8 (IN)

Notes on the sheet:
TX PATH
RX PATH

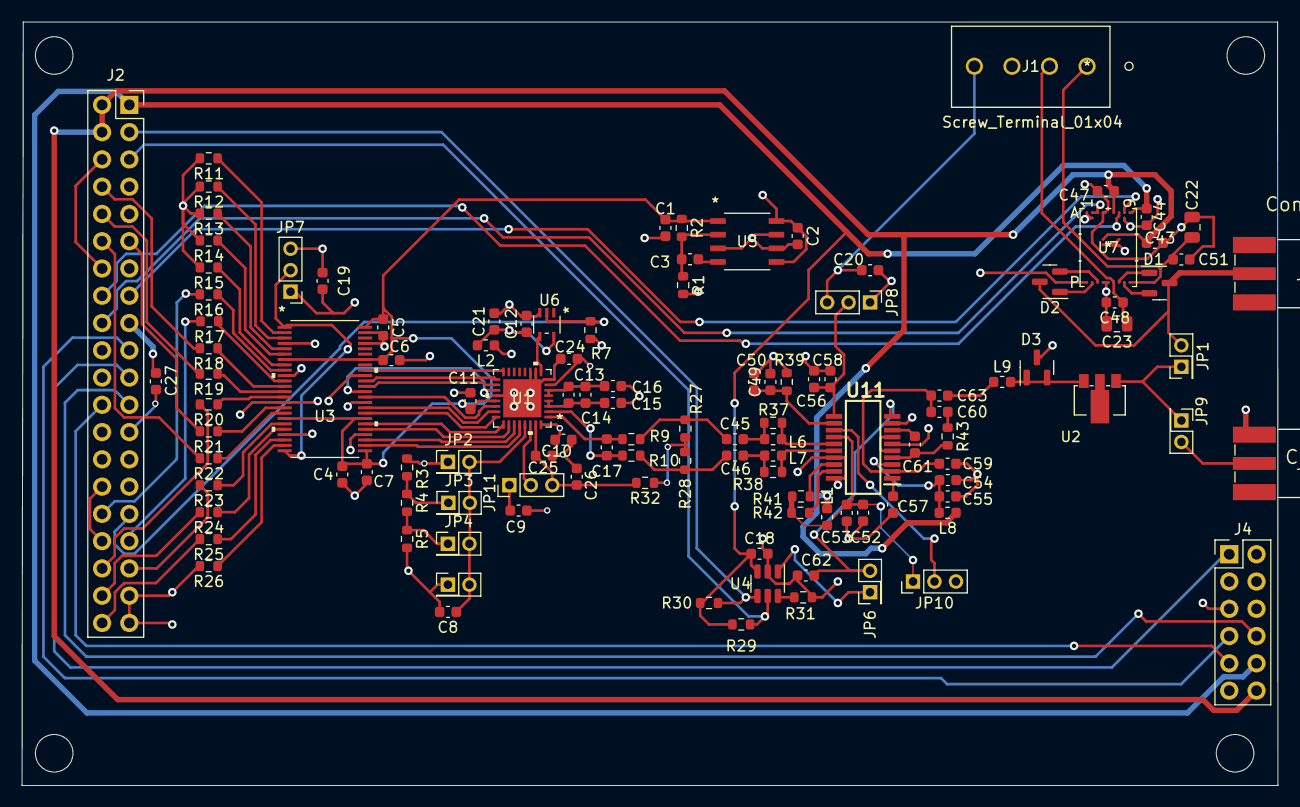
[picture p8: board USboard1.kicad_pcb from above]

Board: 4 copper layers, 117.0 x 71.1 mm, 121 parts (0 on the bottom side), 101 nets.

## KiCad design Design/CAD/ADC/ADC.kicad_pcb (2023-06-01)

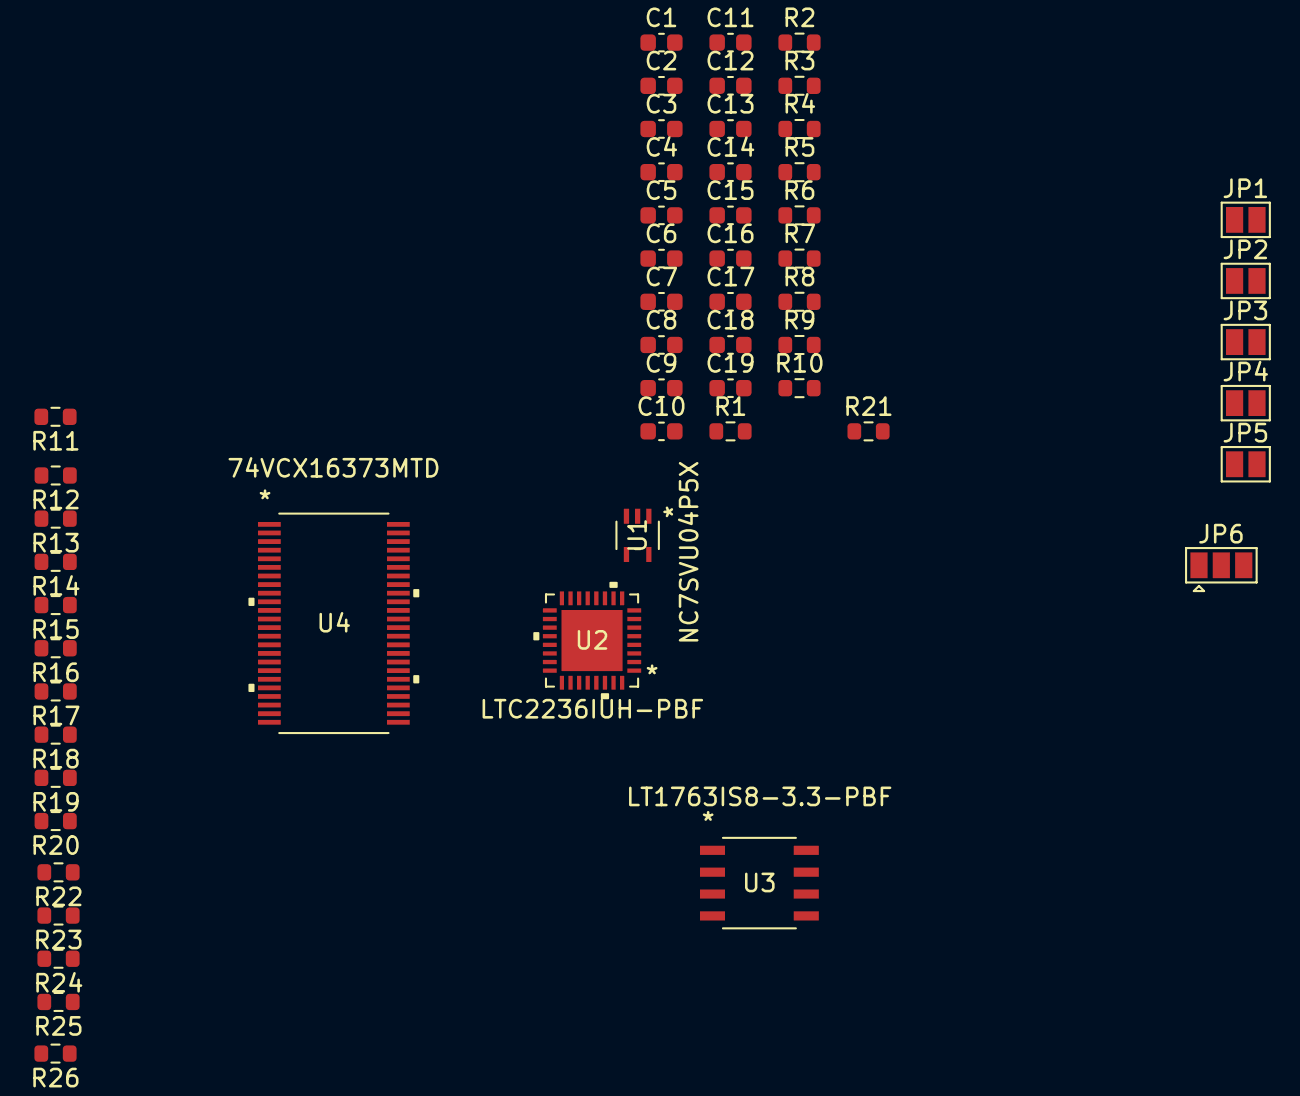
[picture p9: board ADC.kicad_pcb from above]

Board: 2 copper layers, 55 parts (0 on the bottom side), 44 nets, no tracks yet.

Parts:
C1, C2, C5, C9, C10, C13, C14, C16, C17, C18, C19: 0.1u; C_0603_1608Metric
C3: 4.7u; C_0603_1608Metric
C4: 0.2n; C_0603_1608Metric
C6, C7, C15: 1u; C_0603_1608Metric
C8: 2.2u; C_0603_1608Metric
C11: 10uF; C_0603_1608Metric
C12: 0.01u; C_0603_1608Metric
JP1, JP2: Jumper_2_Bridged; SolderJumper-2_P1.3mm_Open_Pad1.0x1.5mm
JP3, JP4, JP5: Jumper_2_Open; SolderJumper-2_P1.3mm_Open_Pad1.0x1.5mm
JP6: Jumper_3_Bridged12; SolderJumper-3_P1.3mm_Open_Pad1.0x1.5mm
R1: 49.9; R_0603_1608Metric
R2, R3: 1k; R_0603_1608Metric
R4, R5: 18; R_0603_1608Metric
R6, R7, R8: 1K; R_0603_1608Metric
R9: 105K; R_0603_1608Metric
R10: 100K; R_0603_1608Metric
R11, R12, R13, R14, R15, R16, R17, R18, R19, R20, R21, R22, R23, R24, R25, R26: 33; R_0603_1608Metric
U1: NC7SVU04P5X
U2: LTC2236IUH-PBF
U3: LT1763IS8-3.3-PBF
U4: 74VCX16373MTD

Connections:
/CLK: R1.1, R2.1, R3.2, U1.2 (A)
GND: C1.2, C2.1, C3.2, C5.1, C6.2, C7.2, C10.2, C11.2, C13.2, C14.2, C15.2, C16.2, C17.2, C18.2, C19.2, JP5.1 (A), R1.2, R2.2, R8.2, R10.2, R11.2, R12.2, R13.2, R14.2, R15.2, R26.2, U1.3 (GND), U2.8 (GND), U2.10 (SHDN), U2.11 (*OE), U2.20 (OGND), U2.31 (VCM), U2.33 (EPAD), U3.3 (GND), U3.6 (GND), U3.7 (GND), U4.4 (GND), U4.10 (GND), U4.15 (GND), U4.21 (GND), U4.28 (GND), U4.34 (GND), U4.39 (GND), U4.45 (GND), U4.47 (I0)
unnamed: C6.1, C8.1, C9.1, U2.3 (REFH), U2.4 (REFH)
unnamed: C7.1, C8.2, C9.2, U2.5 (REFL), U2.6 (REFL)
unnamed: C1.1, JP1.2 (B), U2.30 (SENSE)
unnamed: C10.1, JP2.2 (B), JP3.2 (B), JP4.2 (B), JP5.2 (B), U2.29 (MODE)
unnamed: JP3.1 (A), R6.2, R7.1
unnamed: JP4.1 (A), R7.2, R8.1
unnamed: C13.1, JP6.1 (A)
unnamed: JP6.2 (C), U4.1 (*OE1), U4.24 (*OE2)
unnamed: U1.4 (Y), U2.9 (CLK)
unnamed: C4.1, R4.2, U2.1 (AIN+)
unnamed: C4.2, R5.2, U2.2 (AIN-)
unnamed: U2.16 (D0), U4.40 (I5)
unnamed: U2.17 (D1), U4.38 (I6)
unnamed: U2.18 (D2), U4.37 (I7)
unnamed: U2.19 (D3), U4.36 (I8)
unnamed: U2.22 (D4), U4.35 (I9)
unnamed: U2.23 (D5), U4.33 (I10)
unnamed: U2.24 (D6), U4.32 (I11)
unnamed: U2.25 (D7), U4.30 (I12)
unnamed: U2.26 (D8), U4.29 (I13)
unnamed: U2.27 (D9), U4.27 (I14)
unnamed: U2.28 (OF), U4.26 (I15)
unnamed: C12.2, U3.4 (BYP)
unnamed: C12.1, R9.2, R10.1, U3.2 (SENSE/ADJ)
unnamed: R11.1, U4.2 (O0)
unnamed: R12.1, U4.3 (O1)
unnamed: R13.1, U4.5 (O2)
unnamed: R14.1, U4.6 (O3)
unnamed: R15.1, U4.8 (O4)
unnamed: R16.1, U4.9 (O5)
unnamed: R17.1, U4.11 (O6)
unnamed: R18.1, U4.12 (O7)
unnamed: R19.1, U4.13 (O8)
unnamed: R20.1, U4.14 (O9)
unnamed: R21.1, U4.16 (O10)
unnamed: R22.1, U4.17 (O11)
unnamed: R23.1, U4.19 (O12)
unnamed: R24.1, U4.20 (O13)
unnamed: R25.1, U4.22 (O14)
unnamed: R26.1, U4.23 (O15)
VCC: C11.1, C14.1, C16.1, C17.1, C18.1, C19.1, R9.1, U2.21 (OVDD), U3.1 (OUT), U4.7 (VCC), U4.18 (VCC), U4.25 (LE2), U4.31 (VCC), U4.42 (VCC), U4.48 (LE1)
VDD: C2.2, C3.1, C5.2, C15.1, JP1.1 (A), JP2.1 (A), JP6.3 (B), R3.1, R6.1, U1.5 (VCC), U2.7 (VDD), U2.32 (VDD), U3.5 (*SHDN), U3.8 (IN)

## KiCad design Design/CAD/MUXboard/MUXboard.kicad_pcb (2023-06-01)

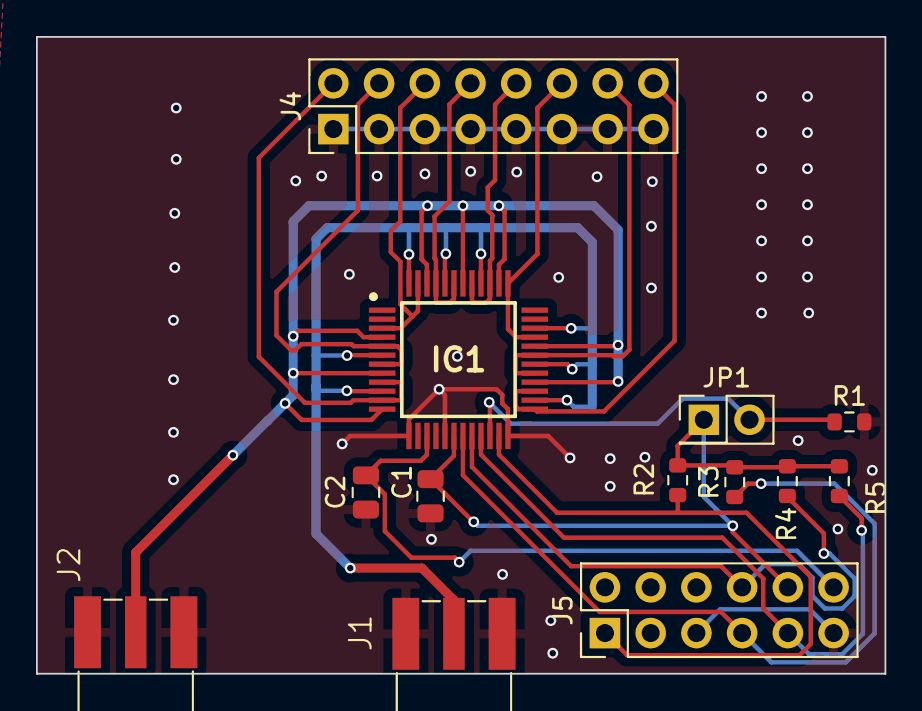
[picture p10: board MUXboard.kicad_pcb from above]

Board: 2 copper layers, 47.1 x 35.4 mm, 13 parts (0 on the bottom side), 18 nets.

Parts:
C1, C2: 1u; C_0805_2012Metric
IC1: HV2607T-C_R8X; QFP50P900X900X160-48N
J1, J2: Conn_Coaxial; RS_526-5785
J4: Conn_01x16_Pin; PinHeader_2x08_P2.54mm_Vertical
J5: Conn_01x12_Pin; PinHeader_2x06_P2.54mm_Vertical
JP1: Jumper_2_Open; PinHeader_2x01_P2.54mm_Vertical
R1, R2, R3, R4, R5: 10K; R_0603_1608Metric

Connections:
+3.3V: C1.1, IC1.18 (VLL), J5.10, JP1.1 (A), R2.2, R3.2, R4.2, R5.2
+5V: C2.1, IC1.15 (VDD), J5.12
/RX: IC1.4 (SW4A), IC1.8 (SW2A), IC1.12 (SW0A), IC1.28 (SW14A), IC1.32 (SW12A), IC1.38 (SW10A), IC1.42 (SW8A), IC1.46 (SW6A), J2.2 (Ext)
/TX: IC1.6 (SW3A), IC1.10 (SW1A), IC1.26 (SW15A), IC1.30 (SW13A), IC1.34 (SW11A), IC1.40 (SW9A), IC1.44 (SW7A), IC1.48 (SW5A), J1.2 (Ext)
/clk: IC1.20 (CLK), J5.8, R4.1
/clr: IC1.22 (CLR), JP1.2 (B), R1.1
/din: IC1.19 (DIN), J5.7, R3.1
/dout: IC1.23 (DOUT), J5.1, R2.1
/le: IC1.21 (~LE), J5.9, R5.1
/tr1: IC1.9 (SW1B), IC1.11 (SW0B), J4.2
/tr2: IC1.5 (SW3B), IC1.7 (SW2B), J4.4 (Pin_2)
/tr3: IC1.3 (SW4B), IC1.47 (SW5B), J4.6 (Pin_3)
/tr4: IC1.43 (SW7B), IC1.45 (SW6B), J4.8 (Pin_4)
/tr5: IC1.39 (SW9B), IC1.41 (SW8B), J4.10 (Pin_5)
/tr6: IC1.33 (SW11B), IC1.37 (SW10B), J4.12 (Pin_6)
/tr7: IC1.29 (SW13B), IC1.31 (SW12B), J4.14 (Pin_7)
/tr8: IC1.25 (SW15B), IC1.27 (SW14B), J4.16 (Pin_8)
GND: C1.2, C2.2, IC1.13 (GND), IC1.17 (DGND), IC1.24 (NC/RGND), J1.3, J1.4, J1.5, J2.3, J2.4, J2.5, J4.1 (Pin_9), J4.3 (Pin_10), J4.5 (Pin_11), J4.7 (Pin_12), J4.9 (Pin_13), J4.11 (Pin_14), J4.13 (Pin_15), J4.15 (Pin_16), J5.5, J5.11, R1.2

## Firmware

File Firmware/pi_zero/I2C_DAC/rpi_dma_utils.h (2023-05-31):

// Raspberry Pi DMA utility definitions; see https://iosoft.blog for details
//
// Copyright (c) 2020 Jeremy P Bentham
//
// Licensed under the Apache License, Version 2.0 (the "License");
// you may not use this file except in compliance with the License.
// You may obtain a copy of the License at
//
//     http://www.apache.org/licenses/LICENSE-2.0
//
// Unless required by applicable law or agreed to in writing, software
// distributed under the License is distributed on an "AS IS" BASIS,
// WITHOUT WARRANTIES OR CONDITIONS OF ANY KIND, either express or implied.
// See the License for the specific language governing permissions and
// limitations under the License.
//
#include <stdint.h>

// Location of peripheral registers in physical memory
#define PHYS_REG_BASE   PI_01_REG_BASE
#define PI_01_REG_BASE  0x20000000  // Pi Zero or 1

//#define CLOCK_HZ      250000000   // Pi 2 - 4
#define CLOCK_HZ        400000000   // Pi Zero

// Location of peripheral registers in bus memory
#define BUS_REG_BASE    0x7E000000

// If non-zero, print debug information
#define DEBUG           0

// If non-zero, set PWM clock using VideoCore mailbox
#define USE_VC_CLOCK_SET 0

// Size of memory page
#define PAGE_SIZE       0x1000
// Round up to nearest page
#define PAGE_ROUNDUP(n) ((n)%PAGE_SIZE==0 ? (n) : ((n)+PAGE_SIZE)&~(PAGE_SIZE-1))

// Structure for mapped peripheral or memory
typedef struct {
    int fd,         // File descriptor
        h,          // Memory handle
        size;       // Memory size
    void *bus,      // Bus address
        *virt,      // Virtual address
        *phys;      // Physical address
} MEM_MAP;

// Get virtual 8 and 32-bit pointers to register
#define REG8(m, x)  ((volatile uint8_t *) ((uint32_t)(m.virt)+(uint32_t)(x)))
#define REG32(m, x) ((volatile uint32_t *)((uint32_t)(m.virt)+(uint32_t)(x)))
// Get bus address of register
#define REG_BUS_ADDR(m, x)  ((uint32_t)(m.bus)  + (uint32_t)(x))
// Convert uncached memory virtual address to bus address
#define MEM_BUS_ADDR(mp, a) ((uint32_t)a-(uint32_t)mp->virt+(uint32_t)mp->bus)
// Convert bus address to physical address (for mmap)
#define BUS_PHYS_ADDR(a)    ((void *)((uint32_t)(a)&~0xC0000000))

// GPIO register definitions
#define GPIO_BASE       (PHYS_REG_BASE + 0x200000)
#define GPIO_MODE0      0x00
#define GPIO_SET0       0x1c
#define GPIO_CLR0       0x28
#define GPIO_LEV0       0x34
#define GPIO_GPPUD      0x94
#define GPIO_GPPUDCLK0  0x98
// GPIO I/O definitions
#define GPIO_IN         0
#define GPIO_OUT        1
#define GPIO_ALT0       4
#define GPIO_ALT1       5
#define GPIO_ALT2       6
#define GPIO_ALT3       7
#define GPIO_ALT4       3
#define GPIO_ALT5       2
#define GPIO_MODE_STRS  "IN","OUT","ALT5","ALT4","ALT0","ALT1","ALT2","ALT3"
#define GPIO_NOPULL     0
#define GPIO_PULLDN     1
#define GPIO_PULLUP     2

// Videocore mailbox memory allocation flags, see:
//     https://github.com/raspberrypi/firmware/wiki/Mailbox-property-interface
typedef enum {
    MEM_FLAG_DISCARDABLE    = 1<<0, // can be resized to 0 at any time. Use for cached data
    MEM_FLAG_NORMAL         = 0<<2, // normal allocating alias. Don't use from ARM
    MEM_FLAG_DIRECT         = 1<<2, // 0xC alias uncached
    MEM_FLAG_COHERENT       = 2<<2, // 0x8 alias. Non-allocating in L2 but coherent
    MEM_FLAG_ZERO           = 1<<4, // initialise buffer to all zeros
    MEM_FLAG_NO_INIT        = 1<<5, // don't initialise (default is initialise to all ones)
    MEM_FLAG_HINT_PERMALOCK = 1<<6, // Likely to be locked for long periods of time
    MEM_FLAG_L1_NONALLOCATING=(MEM_FLAG_DIRECT | MEM_FLAG_COHERENT) // Allocating in L2
} VC_ALLOC_FLAGS;
// VC flags for unchached DMA memory
#define DMA_MEM_FLAGS (MEM_FLAG_DIRECT|MEM_FLAG_ZERO)

// Mailbox command/response structure
typedef struct {
    uint32_t len,   // Overall length (bytes)
        req,        // Zero for request, 1<<31 for response
        tag,        // Command number
        blen,       // Buffer length (bytes)
        dlen;       // Data length (bytes)
        uint32_t uints[32-5];   // Data (108 bytes maximum)
} VC_MSG __attribute__ ((aligned (16)));

// DMA channels and data requests
#define DMA_CHAN_A      10
#define DMA_CHAN_B      11
#define DMA_PWM_DREQ    5
#define DMA_SPI_TX_DREQ 6
#define DMA_SPI_RX_DREQ 7
#define DMA_BASE        (PHYS_REG_BASE + 0x007000)
// DMA register addresses offset by 0x100 * chan_num
#define DMA_CS          0x00
#define DMA_CONBLK_AD   0x04
#define DMA_TI          0x08
#define DMA_SRCE_AD     0x0c
#define DMA_DEST_AD     0x10
#define DMA_TXFR_LEN    0x14
#define DMA_STRIDE      0x18
#define DMA_NEXTCONBK   0x1c
#define DMA_DEBUG       0x20
#define DMA_REG(ch, r)  ((r)==DMA_ENABLE ? DMA_ENABLE : (ch)*0x100+(r))
#define DMA_ENABLE      0xff0
// DMA register values
#define DMA_WAIT_RESP   (1 << 3)
#define DMA_CB_DEST_INC (1 << 4)
#define DMA_DEST_DREQ   (1 << 6)
#define DMA_CB_SRCE_INC (1 << 8)
#define DMA_SRCE_DREQ   (1 << 10)
#define DMA_PRIORITY(n) ((n) << 16)

// DMA control block (must be 32-byte aligned)
typedef struct {
    uint32_t ti,    // Transfer info
        srce_ad,    // Source address
        dest_ad,    // Destination address
        tfr_len,    // Transfer length
        stride,     // Transfer stride
        next_cb,    // Next control block
        debug,      // Debug register, zero in control block
        unused;
} DMA_CB __attribute__ ((aligned(32)));

// PWM controller registers
#define PWM_BASE        (PHYS_REG_BASE + 0x20C000)
#define PWM_CTL         0x00   // Control
#define PWM_STA         0x04   // Status
#define PWM_DMAC        0x08   // DMA control
#define PWM_RNG1        0x10   // Channel 1 range
#define PWM_DAT1        0x14   // Channel 1 data
#define PWM_FIF1        0x18   // Channel 1 fifo
#define PWM_RNG2        0x20   // Channel 2 range
#define PWM_DAT2        0x24   // Channel 2 data
// PWM register values
#define PWM_CTL_RPTL1   (1<<2)  // Chan 1: repeat last data when FIFO empty
#define PWM_CTL_USEF1   (1<<5)  // Chan 1: use FIFO
#define PWM_DMAC_ENAB   (1<<31) // Start PWM DMA
#define PWM_ENAB        1       // Enable PWM
#define PWM_PIN         12      // GPIO pin for PWM output, 12 or 18

// Clock registers and values
#define CLK_BASE        (PHYS_REG_BASE + 0x101000)
#define CLK_PWM_CTL     0xa0
#define CLK_PWM_DIV     0xa4
#define CLK_PASSWD      0x5a000000
#define PWM_CLOCK_ID    0xa

void fail(char *s);
void *map_periph(MEM_MAP *mp, void *phys, int size);
void *map_uncached_mem(MEM_MAP *mp, int size);
void unmap_periph_mem(MEM_MAP *mp);
void gpio_set(int pin, int mode, int pull);
void gpio_pull(int pin, int pull);
void gpio_mode(int pin, int mode);
void gpio_out(int pin, int val);
uint8_t gpio_in(int pin);
void disp_mode_vals(uint32_t mode);
int open_mbox(void);
void close_mbox(int fd);
uint32_t msg_mbox(int fd, VC_MSG *msgp);
void *map_segment(void *addr, int size);
void unmap_segment(void *addr, int size);
uint32_t alloc_vc_mem(int fd, uint32_t size, VC_ALLOC_FLAGS flags);
void *lock_vc_mem(int fd, int h);
uint32_t unlock_vc_mem(int fd, int h);
uint32_t free_vc_mem(int fd, int h);
uint32_t set_vc_clock(int fd, int id, uint32_t freq);
void disp_vc_msg(VC_MSG *msgp);
void enable_dma(int chan);
void start_dma(MEM_MAP *mp, int chan, DMA_CB *cbp, uint32_t csval);
uint32_t dma_transfer_len(int chan);
uint32_t dma_active(int chan);
void stop_dma(int chan);
void disp_dma(int chan);
void init_pwm(int freq, int range, int val);
void start_pwm(void);
void stop_pwm(void);

// EOF

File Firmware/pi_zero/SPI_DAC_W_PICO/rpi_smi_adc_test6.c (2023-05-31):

// Description: SMI ADC test program, using DMA to read ADC samples
#include <stdio.h>
#include <signal.h>
#include <stdint.h>
#include <stdlib.h>
#include <string.h>
#include <unistd.h>
#include "rpi_dma_utils.h"
#include "rpi_smi_defs.h"
#include <math.h>
#include <fcntl.h>     // for O_RDWR
#include <sys/types.h>
#include <sys/stat.h>
#include <fcntl.h>
#include <sys/ioctl.h>
#include <wiringPi.h>
#include <wiringSerial.h>

#define DEVICE "/dev/serial0"
#define BAUD_RATE 115200

// Set zero for single value, non-zero for block read
#define USE_DMA         1
// Use test pin in place of GPIO mode setting (to check timing)
#define USE_TEST_PIN    0

// SMI cycle timings
#define SMI_NUM_BITS    SMI_16_BITS
#define SMI_TIMING      SMI_TIMING_20M

// Timings for RPi v0-3 (1 GHz)
#define SMI_TIMING_1M   10, 25, 50, 25  // 1 MS/s
#define SMI_TIMING_10M   4,  6, 13,  6  // 10 MS/s
#define SMI_TIMING_20M   2,  6, 13,  6  // 20 MS/s
#define SMI_TIMING_25M   2,  5, 10,  5  // 25 MS/s
#define SMI_TIMING_31M   2,  4,  6,  4  // 31.25 MS/s
#define SMI_TIMING_42M   2,  3,  6,  3  // 41.66 MS/s
#define SMI_TIMING_50M   2,  3,  5,  2  // 50 MS/s

// Number of raw bytes per ADC sample
#define SAMPLE_SIZE     2

// Number of samples to be captured, and number to be discarded
#define NSAMPLES        1000
#define PRE_SAMP        100

// Voltage calibration

// GPIO pin numbers
#define ADC_D0_PIN      12
#define ADC_NPINS       10
#define SMI_SOE_PIN     6
#define SMI_SWE_PIN     7
#define SMI_DREQ_PIN    24
#define TEST_PIN        25
#define ADC_NBITS       10
#define ADC_VREF        2
#define ADC_FS          1
#define ADC_ZERO        512
#define ADC_SCALE       0.001953125
// DMA request threshold
#define REQUEST_THRESH  4

// SMI register names for diagnostic print
char *smi_regstrs[] = {
    "CS","LEN","A","D","DSR0","DSW0","DSR1","DSW1",
    "DSR2","DSW2","DSR3","DSW3","DMC","DCS","DCA","DCD",""
};

// SMI CS register field names for diagnostic print
#define STRS(x)     STRS_(x) ","
#define STRS_(...)  #__VA_ARGS__
char *smi_cs_regstrs = STRS(SMI_CS_FIELDS);

// Structures for mapped I/O devices, and non-volatile memory
extern MEM_MAP gpio_regs, dma_regs;
MEM_MAP vc_mem, clk_regs, smi_regs;

// Pointers to SMI registers
volatile SMI_CS_REG  *smi_cs;
volatile SMI_L_REG   *smi_l;
volatile SMI_A_REG   *smi_a;
volatile SMI_D_REG   *smi_d;
volatile SMI_DMC_REG *smi_dmc;
volatile SMI_DSR_REG *smi_dsr;
volatile SMI_DSW_REG *smi_dsw;
volatile SMI_DCS_REG *smi_dcs;
volatile SMI_DCA_REG *smi_dca;
volatile SMI_DCD_REG *smi_dcd;

// Buffer for captured samples
uint16_t sample_data[NSAMPLES];

// Non-volatile memory size
#define VC_MEM_SIZE(nsamp) (PAGE_SIZE + ((nsamp)+4)*SAMPLE_SIZE)

void map_devices(void);
void fail(char *s);
void terminate(int sig);
void smi_start(int nsamples, int packed);
uint32_t *adc_dma_start(MEM_MAP *mp, int nsamp);
int adc_dma_end(void *buff, uint16_t *data, int nsamp);
void init_smi(int width, int ns, int setup, int hold, int strobe);
void disp_smi(void);
void mode_word(uint32_t *wp, int n, uint32_t mode);
float val_volts(int val);
int adc_gpio_val(void);
void disp_reg_fields(char *regstrs, char *name, uint32_t val);
void dma_wait(int chan);
void *dac_thread_func(void *arg);

int main(int argc, char *argv[])
{

    void *rxbuff;
    int i;

    // Initialize WiringPi
    if (wiringPiSetup() == -1) {
        printf("WiringPi setup failed. Maybe you haven't installed it yet?\n");
        return 1;
    }

    // Open the serial port
    int fd = serialOpen(DEVICE, BAUD_RATE);
    if (fd == -1) {
        printf("Could not open serial device %s\n", DEVICE);
        return 1;
    }

    signal(SIGINT, terminate);
    map_devices();
    for (i=0; i<ADC_NPINS; i++)
        gpio_mode(ADC_D0_PIN+i, GPIO_IN);
    gpio_mode(SMI_SOE_PIN, GPIO_ALT1);
    init_smi(SMI_NUM_BITS, SMI_TIMING);
    map_uncached_mem(&vc_mem, VC_MEM_SIZE(NSAMPLES+PRE_SAMP));
    smi_dmc->dmaen = 1;
    smi_cs->enable = 1;
    smi_cs->clear = 1;
    rxbuff = adc_dma_start(&vc_mem, NSAMPLES);
    smi_start(NSAMPLES, 1);

    //Send the READY signal to start pulse and VGA
    serialPuts(fd, "READY");
    usleep(100);
    while (dma_active(DMA_CHAN_A));
    adc_dma_end(rxbuff, sample_data, NSAMPLES);
    disp_reg_fields(smi_cs_regstrs, "CS", *REG32(smi_regs, SMI_CS));
    smi_cs->enable = smi_dcs->enable = 0;
    for (i=0; i<NSAMPLES; i++)
        printf("%1.6f\n", val_volts(sample_data[i]));

    terminate(0);
    serialClose(fd);
    return(0);
}

// Map GPIO, DMA and SMI registers into virtual mem (user space)
// If any of these fail, program will be terminated
void map_devices(void)
{
    map_periph(&gpio_regs, (void *)GPIO_BASE, PAGE_SIZE);
    map_periph(&dma_regs, (void *)DMA_BASE, PAGE_SIZE);
    map_periph(&clk_regs, (void *)CLK_BASE, PAGE_SIZE);
    map_periph(&smi_regs, (void *)SMI_BASE, PAGE_SIZE);
}

// Catastrophic failure in initial setup
void fail(char *s)
{
    printf(s);
    terminate(0);
}

// Free memory segments and exit
void terminate(int sig)
{
    int i;

    printf("Closing\n");
    if (gpio_regs.virt)
    {
        for (i=0; i<ADC_NPINS; i++)
            gpio_mode(ADC_D0_PIN+i, GPIO_IN);
    }
    if (smi_regs.virt)
        *REG32(smi_regs, SMI_CS) = 0;
    stop_dma(DMA_CHAN_A);
    unmap_periph_mem(&vc_mem);
    unmap_periph_mem(&smi_regs);
    unmap_periph_mem(&dma_regs);
    unmap_periph_mem(&gpio_regs);
    exit(0);
}

// Start SMI, given number of samples, optionally pack bytes into words
void smi_start(int nsamples, int packed)
{
    smi_l->len = nsamples + PRE_SAMP;
    smi_cs->pxldat = (packed != 0);
    smi_cs->enable = 1;
    smi_cs->clear = 1;
    smi_cs->start = 1;
}
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

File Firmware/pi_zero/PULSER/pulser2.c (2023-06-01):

#include <stdio.h>
#include <stdlib.h>
#include <wiringPi.h>

// Define the pulse duration in microseconds
#define PULSE_DURATION 5
#define SIZE 3
#define ROWS 3
int main()
{
    // Initialize the GPIO pins
    int pulseA = 3; // GPIO pin 22 (wiringPi pin 3)
    int pulseB = 4; // GPIO pin 23 (wiringPi pin 4)
    int pulseC = 5; // GPIO pin 24 (wiringPi pin 5)

    // Initialize the wiringPi library
    if (wiringPiSetup() == -1)
    {
        printf("Error: Failed to initialize wiringPi library!\n");
        return 1;
    }

    // Set the GPIO pins to output mode
    pinMode(pulseA, OUTPUT);
    pinMode(pulseB, OUTPUT);
    pinMode(pulseC, OUTPUT);

    FILE *file = fopen("pulsestring.txt", "r");
    if (file == NULL) {
        printf("Unable to open file.\n");
        return 1;
    }

    char str[SIZE + 1];
    int pulseSequences[ROWS][SIZE];
    int i = 0;

    while (fgets(str, SIZE + 1, file) != NULL) {
        for (int j = 0; j < SIZE; j++) {
            pulseSequences[i][j] = str[j] - '0'; // Convert char to int
        }
        i++;
        fgetc(file); // To skip the newline character
    }
    fclose(file);

    int numberOfSequences = sizeof(pulseSequences) / sizeof(pulseSequences[0]);

    // Generate the pulses based on the sequences
    printf("Generating pulses...\n");
    for (int i = 0; i < numberOfSequences; i++) {
        digitalWrite(pulseA, pulseSequences[i][0]);
        digitalWrite(pulseB, pulseSequences[i][1]);
        digitalWrite(pulseC, pulseSequences[i][2]);
        delayMicroseconds(PULSE_DURATION);
    }

    return 0;
}

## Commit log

2023-06-01 results and worklog
    [200kHz_0_02V_1M_SPI_PIO_RAMP.csv, 2M_0_02V_20M.csv, 3M_0_02V_20M.csv, 40khz0_02V_31M.csv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]
2023-06-09 new results
    [ADCrampI2C.csv, ADCrampSPI.csv, finalADC.csv]

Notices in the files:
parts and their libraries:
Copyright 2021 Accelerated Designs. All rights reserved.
